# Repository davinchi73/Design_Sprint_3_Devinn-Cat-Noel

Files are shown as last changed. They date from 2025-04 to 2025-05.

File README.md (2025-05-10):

# Design_Sprint_3_Devinn-Cat-Noel

# Switch-Adapted Water Gun Designed for Accessibility

## Overview
We 3.5mm switch-adapted an electric water gun to enable people with limited mobility to enjoy water play. This project involved 3D printing, simple circuitry, and physical prototyping. This water gun is designed as open assistive technology, or OpenAT. This device may be used and adapted by anyone.

## Final Prototype Image
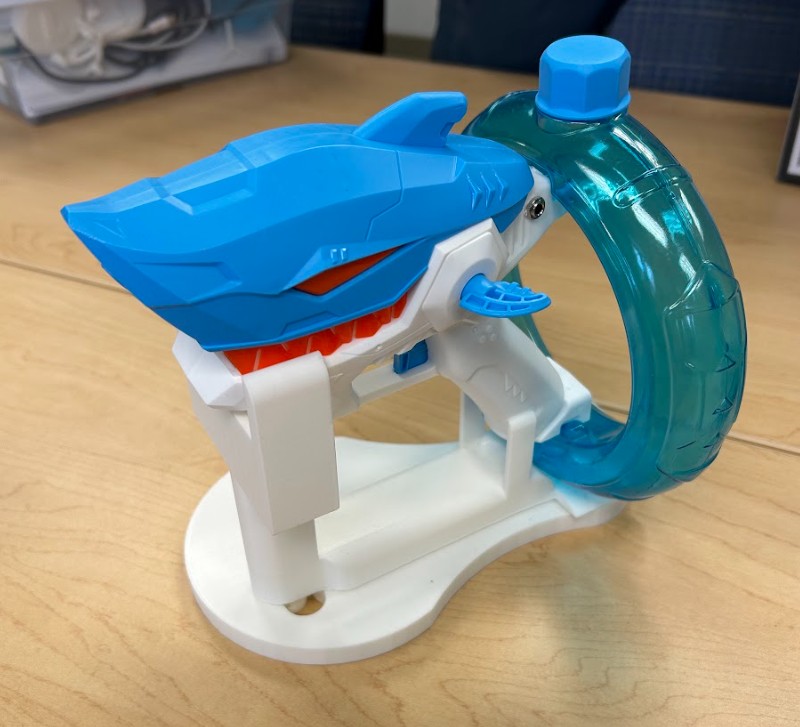
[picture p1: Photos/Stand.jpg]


## Design + Fabrication Summary
- Water gun stand designed using OnShape. 
- Custom stand printed to stabilize the water gun
- Circuitry added using:
  - 3.5 mm jack
  - Momentary Push Button
  - Soldering iron
- **Toy used**: [Electric Water Gun - Shark Water Gun](https://www.walmart.com/ip/Electric-Water-Gun-Shark-Water-Guns-for-Kids-Adults-32FT-Automatic-Squirt-Guns-High-Capacity-Water-Guns-Summer-Water-Play-Toys/15218453861?classType=REGULAR&from=/search)
  - Drilled 1/4" hole for jack  
  - Soldered wires to internal switch and power circuit
 
## How to build this device
All of the files and instructions required to adapted the water gun are contained within this repository. Refer to the Maker Checklist below for more information and documentation.

### 1. Order the components 
Order the necessary components for this build. They are listed in the [bill of materials](https://github.com/davinchi73/Design_Sprint_3_Devinn-Cat-Noel/blob/main/Documentation/Water_Gun_Bill_of_Materials.pdf). 

### 2. Print the 3D printables
Print the files using a 3D printer. We used [Prusa](https://www.prusa3d.com/?utm_source=google&utm_medium=cpc&utm_campaign=EN-US_Search_Text_Brand&utm_id=805226342&gad_source=1&gad_campaignid=805226342&gbraid=0AAAAADkiZoMQLWx7I6_i8Z4JGoRqfIOiK&gclid=Cj0KCQjwoNzABhDbARIsALfY8VMpwMWZt9w00vws5xpJP1zPjw0NuY0tMLbhMrT6I6lO_lXg2FqFplsaAkaQEALw_wcB) and [Bambu](https://us.store.bambulab.com/?gad_source=1&gad_campaignid=20326984537&gbraid=0AAAAAo9so7M-KN1elnPLE1mRjUI4ZcQL0&gclid=Cj0KCQjwoNzABhDbARIsALfY8VO-hWUIrqNfUYTLE7RObMGa2J3tRXY2lEzaHcmRl2_5EFsTW3EwSZIaArtVEALw_wcB) devices for our project. The printable files are linked below in the "Files" section of this readme.

### 3. Assemble the water gun
Refer to the [assembly guide](https://github.com/davinchi73/Design_Sprint_3_Devinn-Cat-Noel/blob/main/Documentation/Water_Gun_Assembly_Guide.pdf) for the instructions on how to assemble this device. This includes the tools and other things necessary for assembly.

## Files

### Build Files
[.stl files of Swivel Plate and Water Gun Stand](https://github.com/davinchi73/Design_Sprint_3_Devinn-Cat-Noel/tree/main/Build_Files)

### Design Files
[.obj files of Swivel Plate and Water Gun Stand](https://github.com/davinchi73/Design_Sprint_3_Devinn-Cat-Noel/tree/main/Design_Files)

### Documentation
| Document              | Version | Link |
|-----------------------|---------|------|
| Assembly Guide        | 1.0     | [Switch Adapted Water Gun Assembly Guide](/Documentation/Water_Gun_Assembly_Guide.pdf)|
| Design Rationale      | 1.0     | [Switch Adapted Water Gun Design Rationale](/Documentation/Water_Gun_Stand_Design_Rationale.pdf)|
| Printing Guide        | 1.0     | [Switch Adapted Water Gun Printing Guide](/Documentation/Water_Gun_3D_Printing_Guide.pdf)|
| Maker Checklist       | 1.0     | [Switch Adapted Water Gun Maker Checklist](/Documentation/Switch_Adapted_Water_Gun_Maker_Checklist_v1.0.pdf)|
| User Guide            | 1.0     | [Switch Adapted Water Gun User Guide](/Documentation/Water_Gun_User_Guide.pdf)|
| Changelog             | 1.0     | [Switch Adapted Water Gun Changelog](/Documentation/Switch_Adapted_Water_Gun_Changelog_v1.0.pdf)|

## Acknowledgments
- Toy adaption designed by Kerilyn Kennedy – Makers Making Change 
- 3D Printed Water Gun Stand designed by Devinn Chi, Cat Martins, and Noel Raehl
- Documentation by Devinn Chi, Cat Martins, and Noel Raehl

Based on the OpenAT format by Makers Making Change – [OpenAT Template](https://github.com/makersmakingchange/OpenAT-Template)

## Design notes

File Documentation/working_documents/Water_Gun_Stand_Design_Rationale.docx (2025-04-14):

# Overview

The Design Rationale is intended to provide designers and maker information about the design process and design decisions behind the development of the Water Gun Stand, a 3D printable stand that is accessible for users and easy to use.

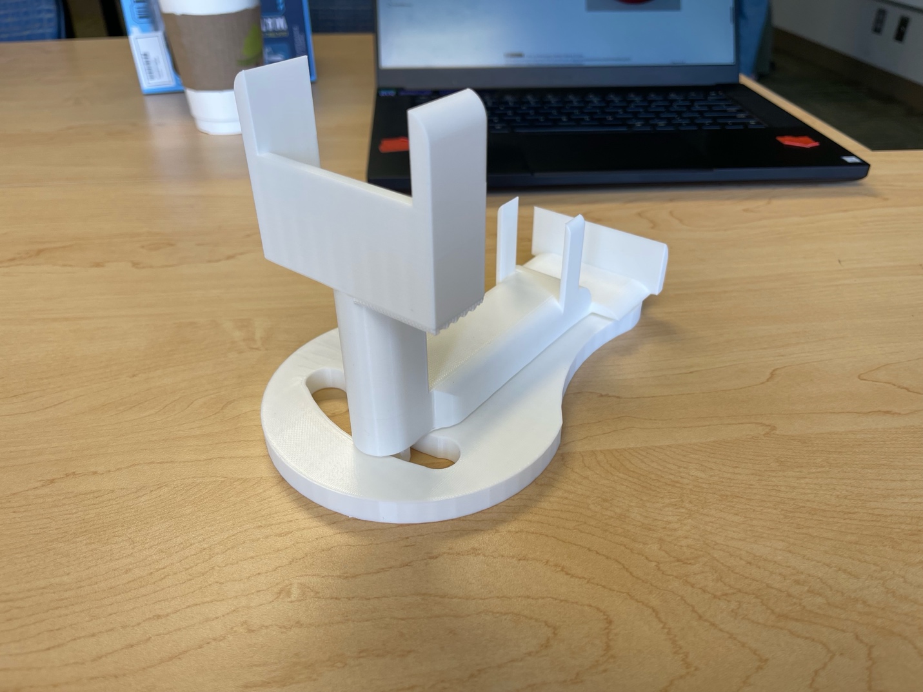
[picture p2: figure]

# Introduction

We were inspired to create a stand for a water gun to the MMC library by Lauren Milne, a professor at Macalester College who is teaching our Human Computer Interaction class. People who are otherly-abled may not be able to hold or operate a water gun as others can. Operations of water guns includes being able to pull a trigger or pump the pressure tank, and hold/aim the water gun muzzle at objects or people.

# Requirements

The goals and requirements outlined here can be used to assess if a device would meet the needs of a user, and determine when a design is sufficient for release.

## Goals

G01 | Design a 3D printed stand for the water gun
G02 | Switch adapt the water gun
G03

## Functional Requirements

F01 | The water gun works with a 3.5 mm switch
F02
F03

## Non-functional Requirement

NF01 | Using this adaptation should be easy, and doable for other volunteer makers can do it themselves
NF02
NF03

## Constraints

C01
C02
C03

# Ideation

The water fun planned to be used in this project is shown below. It is a battery-operated water gun that required no pumping to squirt water out. It can be purchased here (https://www.walmart.com/ip/Tcovle-Electric-Shark-Water-Blaster-Super-Squirter-Fast-Fill-33-ft-Long-Range-Soaker-Toys-Summer-Swimming-Pool-Beach-Party-Backyard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). The idea we are attempting to solidify is to first add a 3.5 mm jack in parallel with the existing switch in the water gun, then create a stand that can hold the gun upwards and in firing position. Below is the gun which we were planning on using.

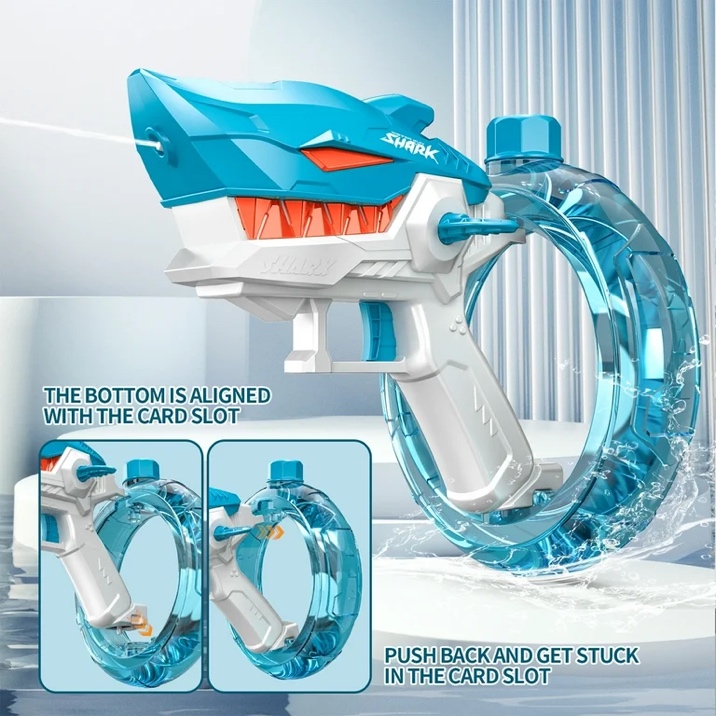
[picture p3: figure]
Original Water gun

# Conceptual Designs

## CONCEPT 1 – Adding the adapted switch in parallel

The original concept for the water gun adaptation was to be able to use ideas from existing MMC designs, more specifically this switch adapted water gun (https://github.com/makersmakingchange/Switch-Adapted-Water-Gun/tree/main), this interact switch (https://github.com/makersmakingchange/Interact-Switch), and this light switch (https://github.com/makersmakingchange/Light-Touch-Switch), and adapt the water gun to be able to fire alongside the existing trigger. Once this was complete, we would ideally be able to create a base for the water gun that would be able to stably support it, as well as offer functionality for aiming. To access the internals of the water gun, including the wiring which we would need to modify for wiring our switches in parallel, we needed to unscrew various screws located on the gun, and once those were removed we simply pulled the gun apart. Once this was done, we drilled a small hole in an accessible part of the gun displayed below.

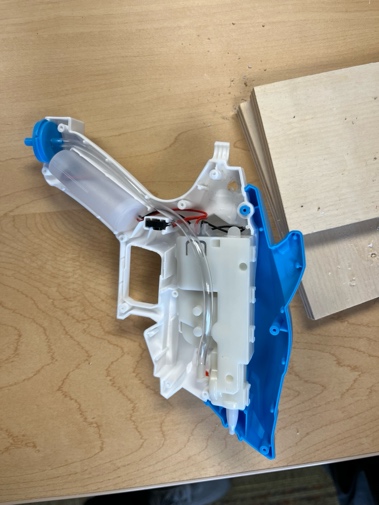
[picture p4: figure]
Hole drilled in water gun for 3.5 mm jack

After this was completed, we worked on wiring the gun in parallel by soldering connections within the gun and connecting them to the 3.5 mm jack. Once this was done, we screwed the gun back together and connected the battery. Below are images depicting the spot we chose for the 3.5 mm jack.

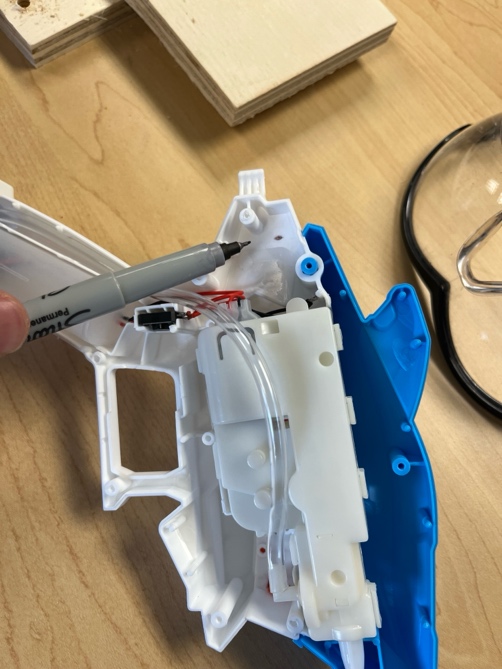
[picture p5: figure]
where we chose to drill
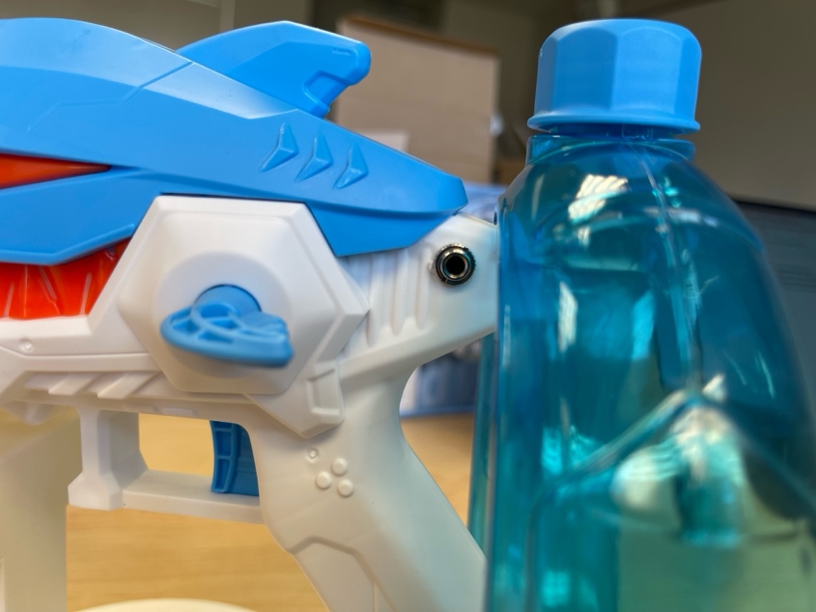
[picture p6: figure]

# Testing

We tested this concept by plugging in the interact switch (https://github.com/makersmakingchange/Interact-Switch) and the light switch (https://github.com/makersmakingchange/Light-Touch-Switch), and testing the firing mechanic to make sure it fired using the adapted switches. We also made sure that the original trigger still worked.

## CONCEPT 2 – Creating the 3D printable stand

Next, we wanted to create a stand that would be a be able to hold the gun in an upright position, and allow for easy access to aiming capabilities. We did this by creating our 3D model in Onshape (https://www.onshape.com/en/), and developing this initial model:

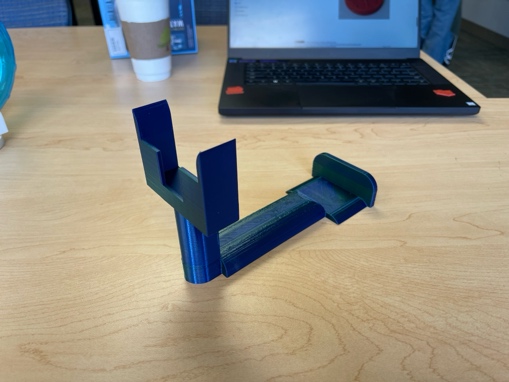
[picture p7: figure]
initial model image

This model was a bit too loose, so the water gun would shift around and not stay in place as intended. Mainly, the rear portion of the water gun would slide around too much, and the front prongs of the stand were not tight enough, so the gun would be overall unstable. This led us to create a second design:

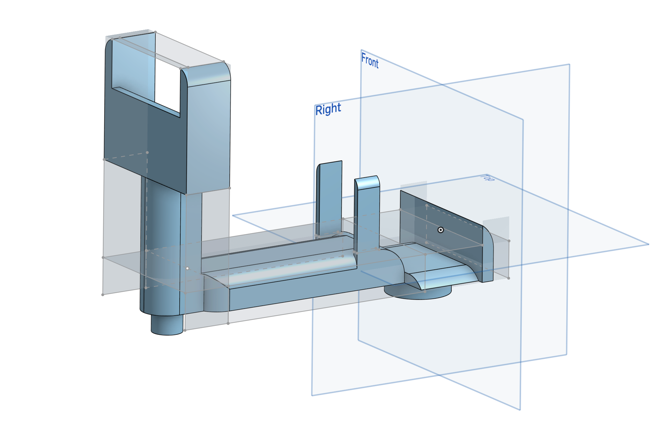
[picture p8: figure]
stand v2 3d model
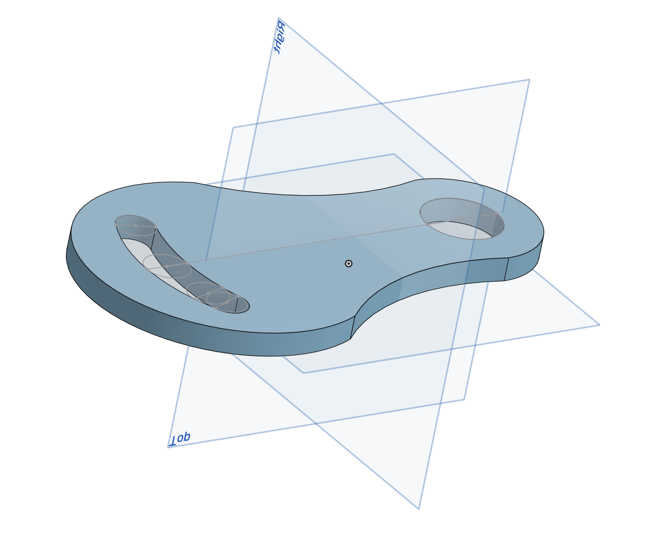
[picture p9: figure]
slide plate 3d model

This design included adjustments in dimensions which allowed for the gun to be more stable in the stand. These included shortening the distance between the front prongs which hold on to the head of the gun, and adding small supports near the rear of the stand that would hold the rear of the gun in place. This worked wonders, as depicted below:

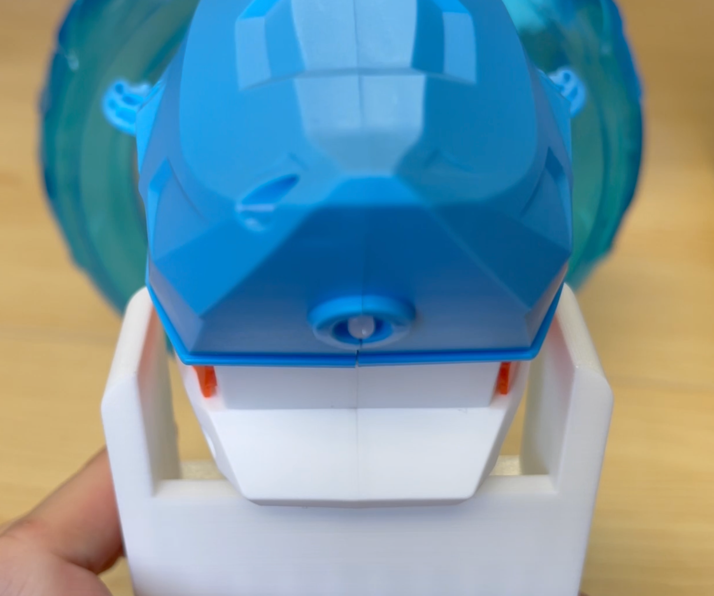
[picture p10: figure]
gap in prongs is reduced
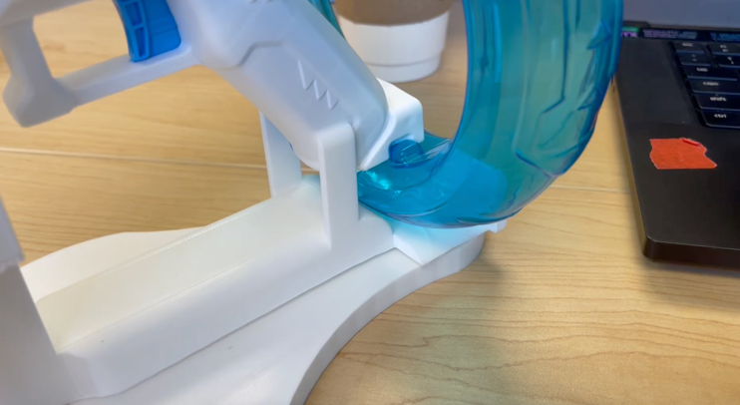
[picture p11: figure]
supports are included to hold gun in place

Once this was done, we added swivel functionality by including the printable swivel plate, which attaches to the water gun stand by using two small cylinders that correspond to cutouts in the swivel plate. The final design is shown below:

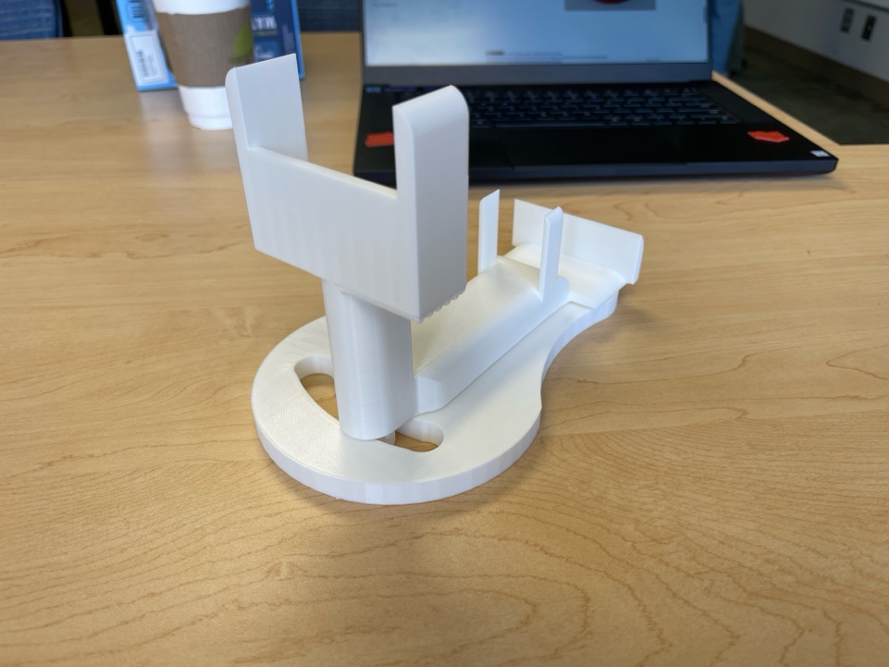
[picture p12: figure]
final design

This design allows for easy aiming in a small arc shape.

# Detailed Design

Above is the final version of our water gun stand, alongside the swivel plate.

# Opportunities for Improvement

- Add a larger swivel plate so that the user can aim in a wider arc
- Add adaptations to the stand so that the user can aim vertically
- Add rubber base to the swivel plate so that it does not slide around on surfaces

© 2025 by Devinn Chi & Cat Martins & Noel Raehl This work is licensed under the CC BY SA 4.0 License: http://creativecommons.org/licenses/by-sa/4.0 Files available at https://github.com/davinchi73/Design_Sprint_3_Devinn-Cat-Noel/tree/main Page 1 of 1

V1.0.1 | April 2025 Water gun Stand Design Rationale

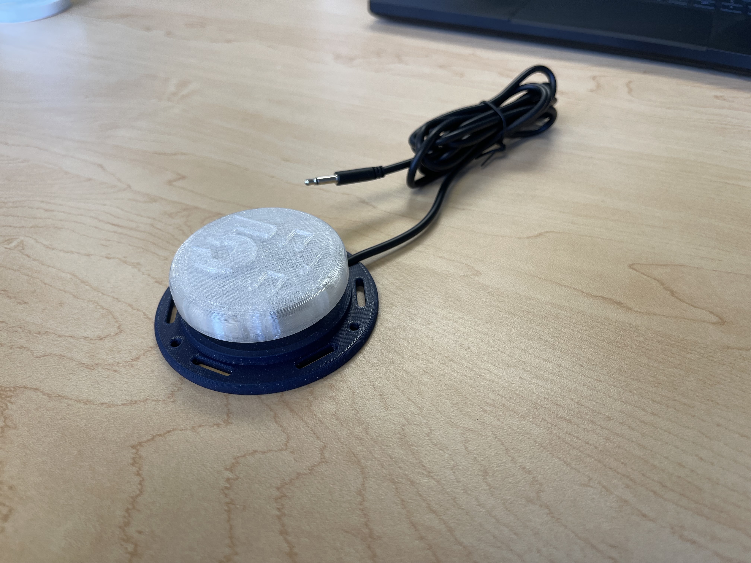
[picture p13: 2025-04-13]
Photos/Interact_Switch_Sideview.jpg

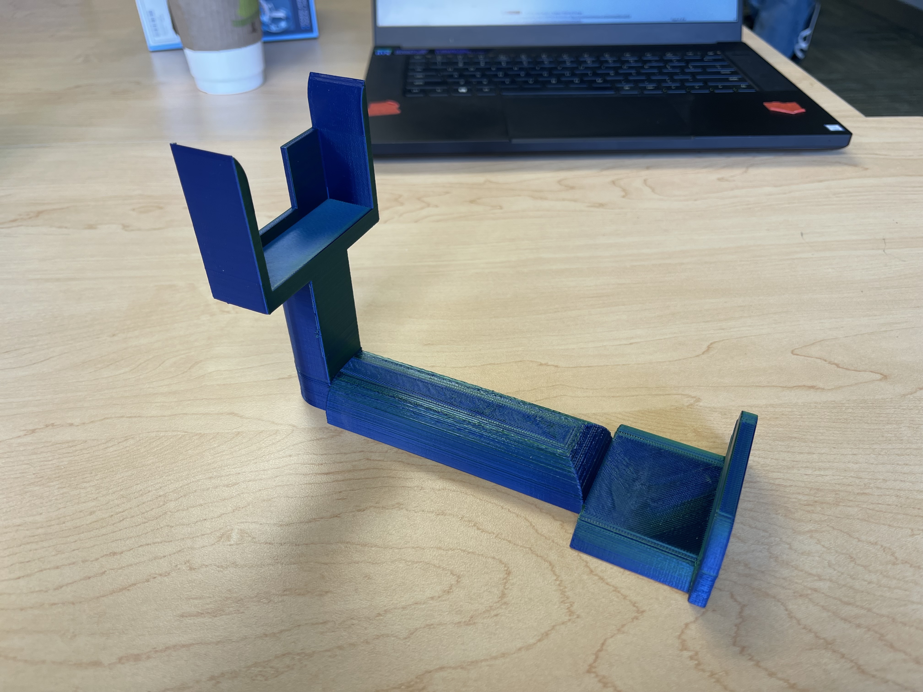
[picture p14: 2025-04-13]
Photos/Stand_V1_Sideview.jpg

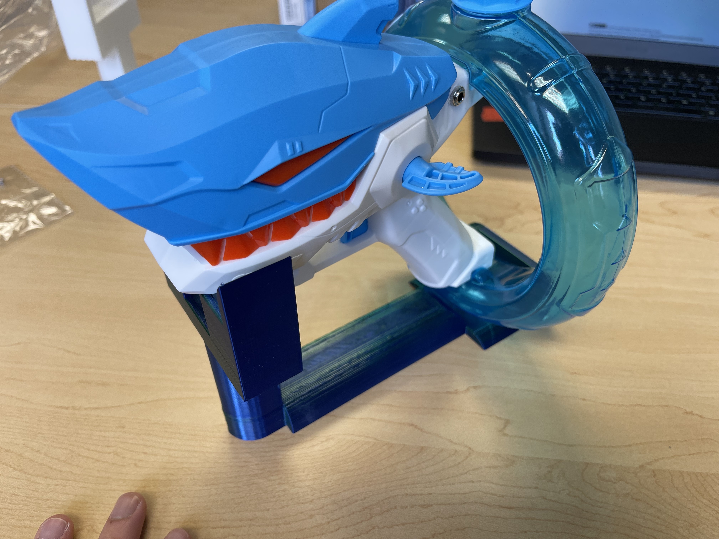
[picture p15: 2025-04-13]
Photos/Gun_and_V1Stand.jpg

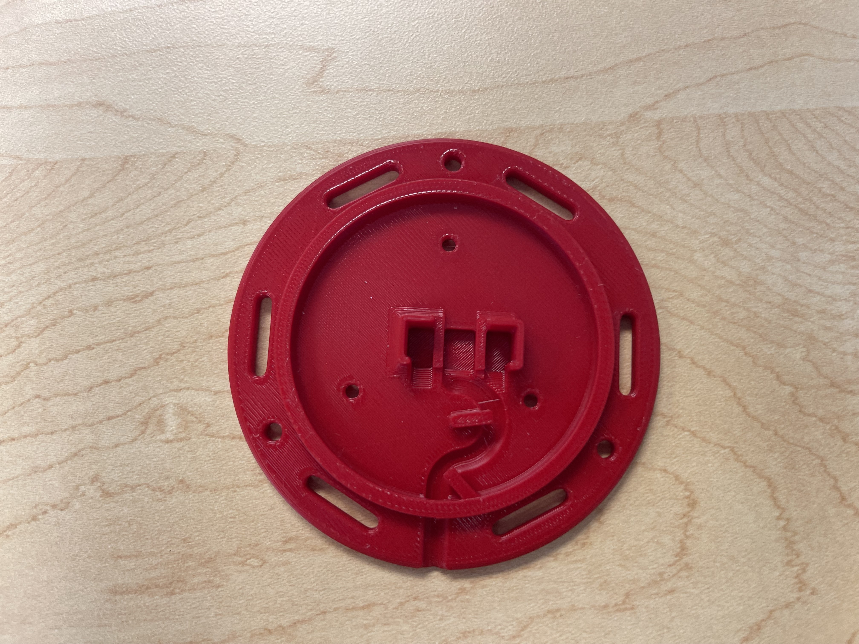
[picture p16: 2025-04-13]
Photos/Interact_Switch_Baseplate.jpg

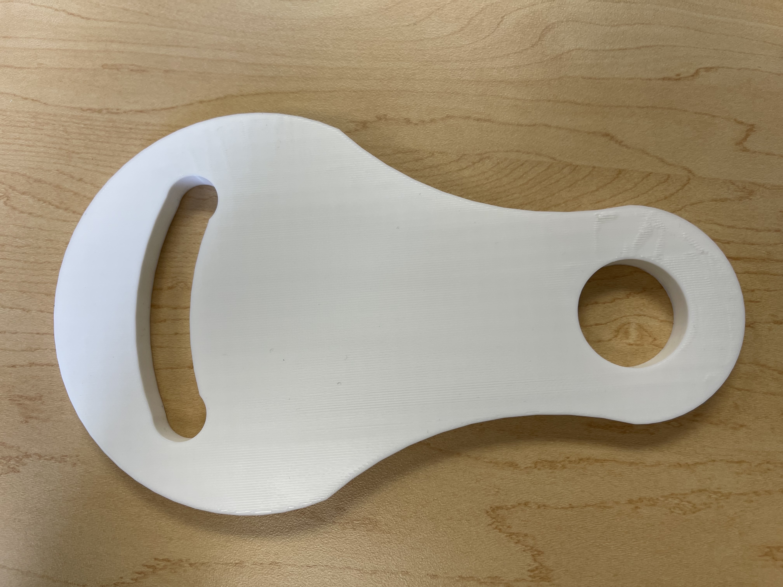
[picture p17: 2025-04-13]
Photos/Swivel_Plate_Birdseyeview.jpg

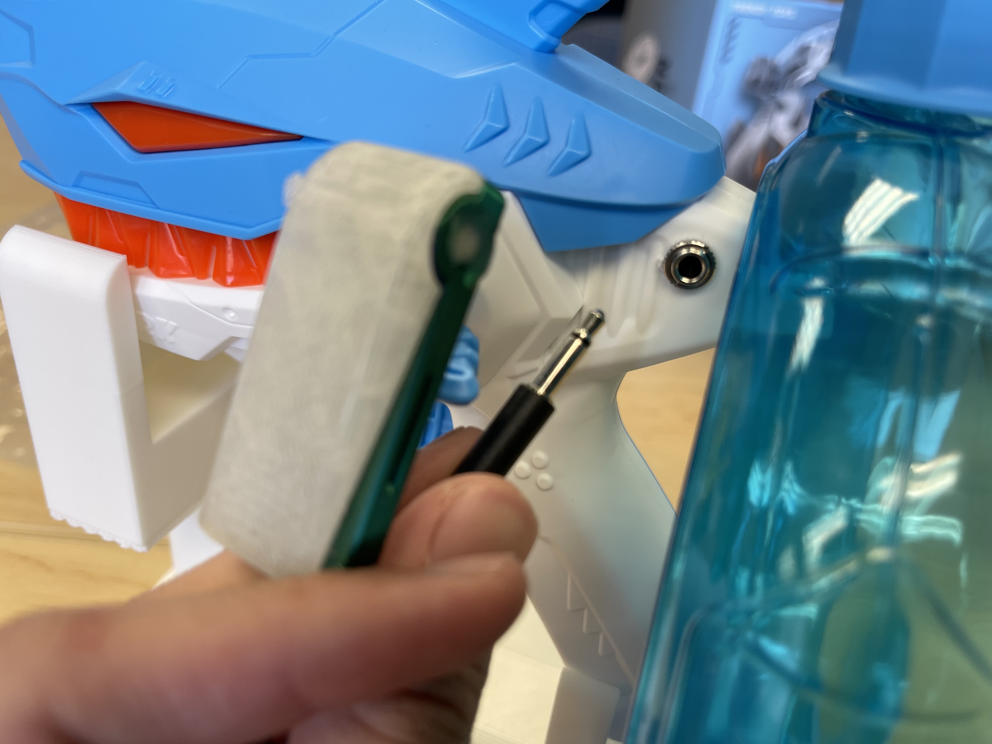
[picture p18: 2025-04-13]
Photos/Watergun_3.5_port_2.jpg

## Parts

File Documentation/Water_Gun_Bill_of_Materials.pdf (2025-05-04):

# Switch Adapted Water Gun

Version: V1.0.1 | Date Created: APRIL 2025

Part type (Electrical. Mechanical, Sanitization, ect)
Electric Water Gun
3.5mm Mono Jack
Copper Wire
3.5mm Nut
3D Printed Parts | ESTIMATED PRICING USING 1KG ROLL COST: | $ | 30.00
Part
Water Gun Stand
Part and description | Link
Electric water gun found on Amazon | Electric Water Gun (https://www.amazon.com/Electric-Adults-Strong-Capacity-Outdoor/dp/B0D2Y83WL4?gQT=1)

Alternatives

Commercial Parts:

Total Cost | Total Print time (hr) | Total filament (g)
$ | 18.49 | 7.77 | 205.68
Quantity Needed | Pkg Quantity | Price per package | Price per Unit | Price for qty needed | Link
1 | 1 $ | 10.00 | $ | 10.00 | $ | 10.00 | Electric Shark Water Gun - Walmart (https://www.walmart.com/ip/Tcovle-Electric-Shark-Water-Blaster-Super-Squirter-Fast-Fill-33-ft-Long-Range-Soaker-Toys-Summer-Swimming-Pool-Beach-Party-Backyard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)
1 | 1 $ | 2.14 | $ | 2.14 | $ | 2.14 | Jack - Digikey (https://www.digikey.ca/short/pq1d1z)
1 | 100 $ | 8.99 | $ | 0.09 | $ | 0.09 | Copper Wire - Amazon (https://www.amazon.com/Copper-Gardening-Electroculture-Jewelry-Diameter/dp/B0C8SFPY7B)
1 | 100 $ | 9.29 | $ | 0.09 | $ | 0.09 | Nut - Amazon (https://www.amazon.com/uxcell-Metric-Thread-Stainless-Fastener/dp/B0143GL8WA)
Quantity Needed | TOTAL Mass (g) | Estimated Price | Print Time (Min)
1 | 205.68 | $ | 6.17 | 466
Total Print Cost: | $ | 6.17

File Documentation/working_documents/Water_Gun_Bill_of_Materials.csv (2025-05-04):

Switch Adapted Water Gun |  | Total Cost | Total Print time (hr) | Total filament (g)
Version: V1.0.1 | Date Created: APRIL 2025 | $18.49 | 7.77 | 205.68
Commercial Parts:
Part type (Electrical. Mechanical, Sanitization, ect) |  | Quantity Needed | Pkg Quantity | Price per package | Price per Unit | Price for qty needed | Link
Electric Water Gun |  | 1 | 1 | $10.00 | $10.00 | $10.00 | Electric Shark Water Gun - Walmart
3.5mm Mono Jack |  | 1 | 1 | $2.14 | $2.14 | $2.14 | Jack - Digikey
Copper Wire |  | 1 | 100 | $8.99 | $0.09 | $0.09 | Copper Wire - Amazon
3.5mm Nut |  | 1 | 100 | $9.29 | $0.09 | $0.09 | Nut - Amazon
3D Printed Parts ESTIMATED PRICING USING 1KG ROLL COST: | $30.00
Part |  | Quantity Needed | TOTAL Mass (g) | Estimated Price | Print Time (Min)
Water Gun Stand |  | 1 | 205.68 | $6.17 | 466
 |  |  | Total Print Cost: | $6.17
Alternatives
Part and description | Link
Electric water gun found on Amazon | Electric Water Gun

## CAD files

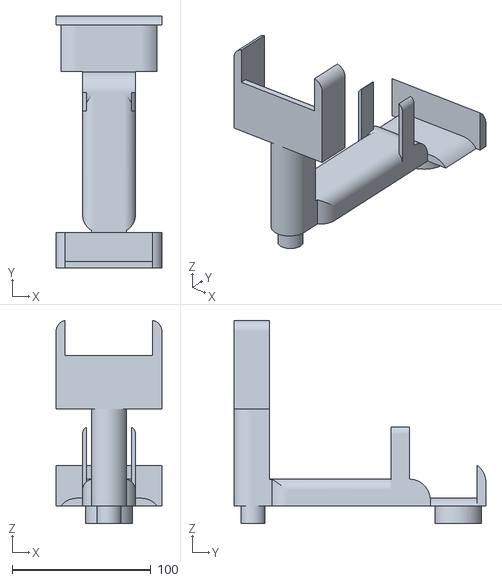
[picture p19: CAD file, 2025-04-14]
Build_Files/water_gun_stand_v2.stl
76.2 x 181.4 x 146.1

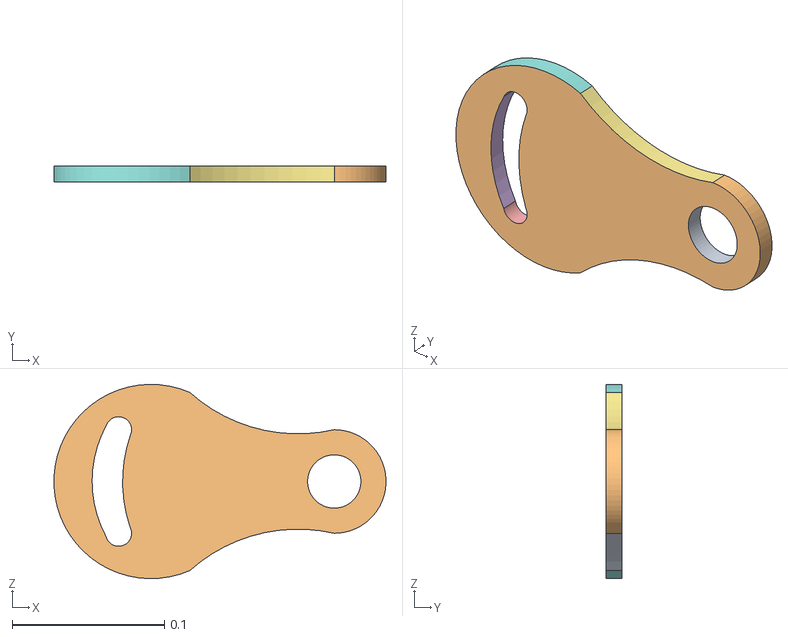
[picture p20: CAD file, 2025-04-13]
Design_Files/swivel plate.obj
0.218 x 0.0108 x 0.127

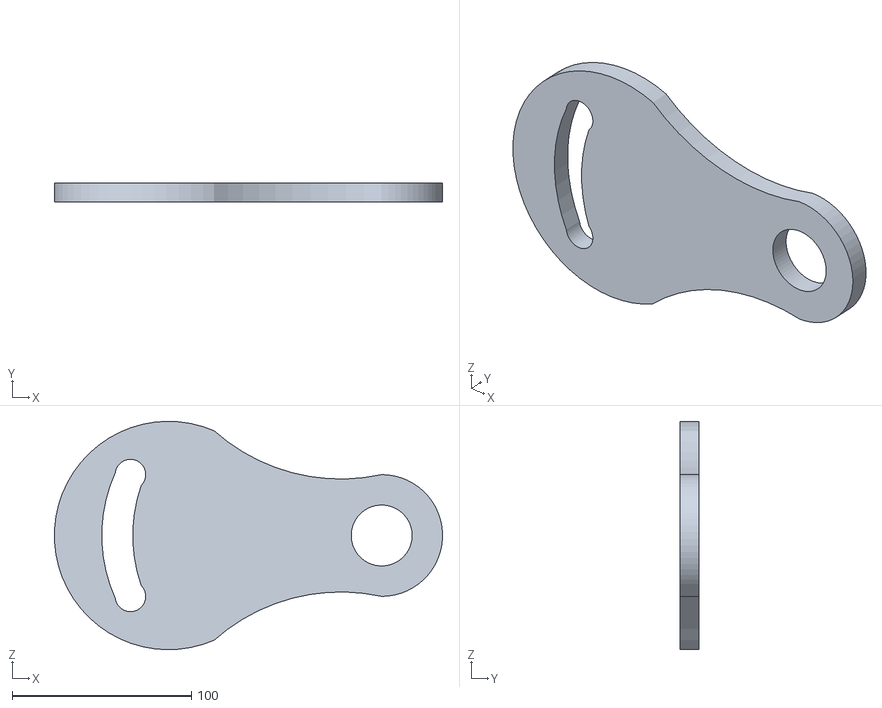
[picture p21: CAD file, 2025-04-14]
Build_Files/swivel_plate.stl
216.6 x 10.8 x 127.5

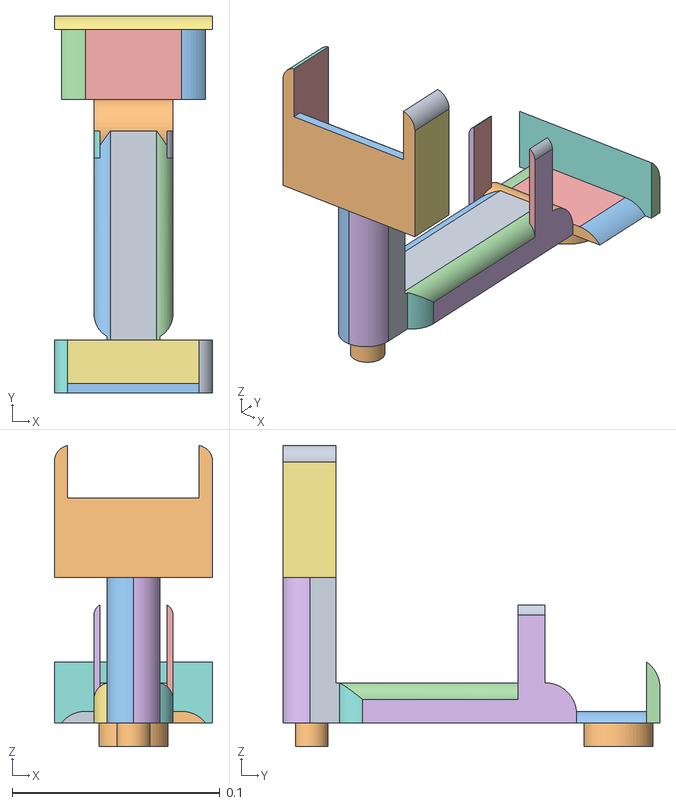
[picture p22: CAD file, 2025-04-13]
Design_Files/Water_gun_stand.obj
0.0762 x 0.181 x 0.145

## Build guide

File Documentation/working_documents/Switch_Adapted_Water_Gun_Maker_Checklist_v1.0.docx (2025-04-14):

V1.0 | April 2025

Switch Adapted Water Gun

MAKER CHECKLIST

Maker To Do List

| Read through the Assembly Guide to become familiar with required components, tools, supplies, and safety gear and overall assembly steps.
| Ask the User if they already own a 4mm switch
| Talk to the User about customization options (e.g., color, any special requests, etc.)
| Order hardware components.
| Gather tools, supplies, and safety equipment.
| Adapt the Water Gun.
| Print and assemble 3D Printed Water Gun Stand.
| Test device.
| Print “User Quick Guide.”

Items to Give to User

Adapted Water Gun.

“User Quick Guide.”

© 2025 by Devinn Chi & Cat Martins & Noel Raehl
This work is licensed under the CC BY SA 4.0 License: http://creativecommons.org/licenses/by-sa/4.0 Files available at https://github.com/davinchi73/Design_Sprint_3_Devinn-Cat-Noel/tree/main

Page 1 of 1

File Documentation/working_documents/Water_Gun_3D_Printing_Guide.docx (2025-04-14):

# 3D Printing Summary (Prusa MK4)

Metrics | Water Gun Stand
Total Print Time (min) | 466min
Total Number of Components | 2
Typical Total Mass (g) | 205.68g
Typical Number of Print Setups | 1

# 3D Printing Settings (Prusa MK4)

Print File Name | Qty | Total Print Time (hr:min) | Mass (g) | Infill (%) | Support (Y/N) | Layer Height/ Nozzle Diameter (mm) | Notes (orientation, special settings, etc.)
water_gun_stand_v2.stl + swivel_plate.stl | 1 | 7:46 | 205.68g | 15 | Y (on build plate only) | 0.3/0.4 | Print in orientation given in STL Used 0.20mm structural rather than speed

# Post-Processing

It is good to use supports for this device. I chose to let my slicer program, the Prusa slicer, automatically insert supports on the build plate only. I also chose to use 0.20mm structural instead of speed, so that the build has a higher chance of being printed stably.

# Customization Options

The user can request the colour of the stand or any other custom markings they may want on the device.

# Examples of Quality Prints

Below are pictures of what the quality of the print is expected to look like.

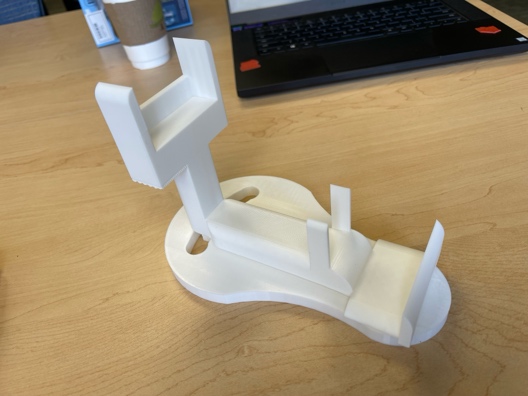
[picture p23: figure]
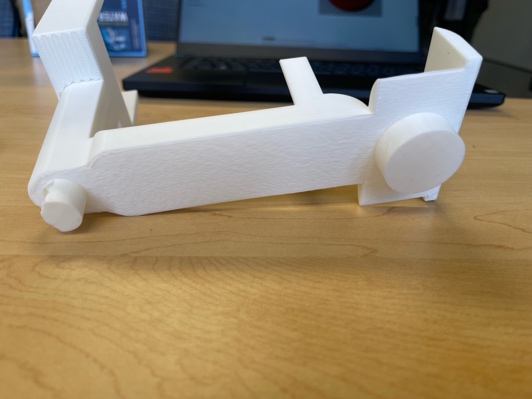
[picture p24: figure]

© 2025 by Devinn Chi, Cat Martins, Noel Raehl – Macalester College This work is licensed under the CC BY SA 4.0 License: http://creativecommons.org/licenses/by-sa/4.0 Files available at https://github.com/davinchi73/Design_Sprint_3_Devinn-Cat-Noel Page 1 of 2

V1.0.1 | April 2025 Water Gun Stand 3D Printing Guide

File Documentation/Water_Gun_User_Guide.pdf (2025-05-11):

V1.0.1 | April 2025

### Switch-Adapted Water Gun – User Guide

### Overview

This water gun has been adapted for accessibility and can be activated using a 3.5mm external switch.

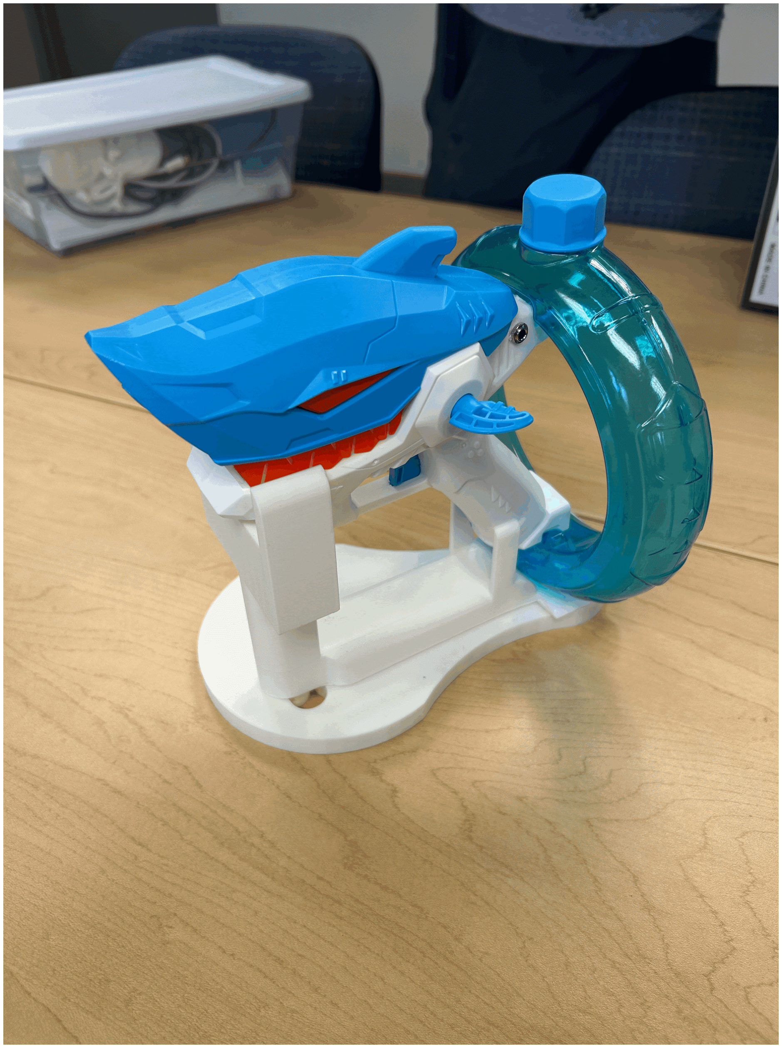
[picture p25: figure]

### Parts / Included Components

This water gun comes with:

- Shark Water Gun – The main toy, changed so it works with a switch
- 3D Printed Stand – Helps hold the gun upright when not in use
- 3.5mm Jack (built-in) – Where you plug in the switch

### Features

- Works with a button switch
- Uses a standard 3.5mm plug
- Just add batteries and plug it in to use

### Usage

- Putting in Batteries: Use a screwdriver to open the toy. The battery compartment is inside the handle. Insert 2 AA batteries, then screw it closed again.
- Using the Gun: Plug in the switch and press the button to spray
- Storing It: Take the batteries out if you're not using it for a while

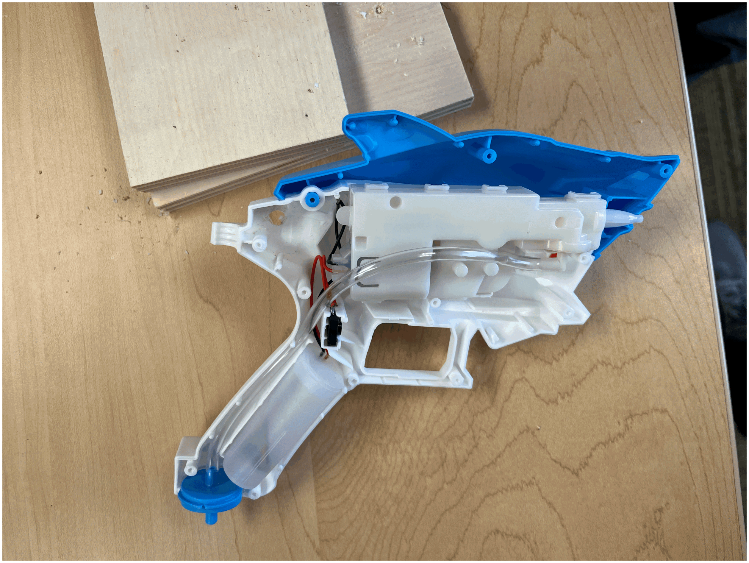
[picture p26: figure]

To replace the batteries, begin by unscrewing the screws that secure both halves of the toy’s outer shell. Once opened, you’ll find the battery compartment located in the handle, just below the trigger. Rotate the old batteries out and insert the new ones as indicated.

### Care and Cleaning

- Wipe the water gun with a damp cloth
- Don’t put it in water
- Keep the switch and plug dry
- Store it somewhere cool and out of the sun

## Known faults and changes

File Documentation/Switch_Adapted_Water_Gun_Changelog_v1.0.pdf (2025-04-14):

V1.0 | April 2025

# Switch Adapted Water Gun CHANGELOG

# Version 1.0 | Date 04/13/2025

## - Ini%al Version - Toy adap%on designed by Kerilyn Kennedy – Makers Making Change - 3D Printed Water Gun Stand designed by Devinn Chi, Cat Mar%ns, and Noel Raehl - Documenta%on by Devinn Chi, Cat Mar%ns, and Noel Raehl

© 2025 by Devinn Chi & Cat Martins & Noel Raehl This work is licensed under the CC BY SA 4.0 License: http://creativecommons.org/licenses/by-sa/4.0 Files available at https://github.com/davinchi73/Design_Sprint_3_Devinn-Cat-Noel/tree/main

Page 1 of 1

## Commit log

2025-04-13 pushed build files
    [Water_gun_stand.obj, swivel plate.obj]
2025-04-14 design and build files upload
    [Water_gun_stand.obj, swivel plate.obj, swivel_plate.stl, water_gun_stand_v2.stl]
2025-04-14 3d print guide
2025-05-04 bill of materials
    [Water_Gun_Bill_of_Materials.csv]
2025-05-11 Battery Change Details/Image to User Guide
